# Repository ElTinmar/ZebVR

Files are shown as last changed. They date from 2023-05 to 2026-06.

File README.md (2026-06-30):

# ZebVR

Virtual reality for zebrafish.

<!---TODO
Add screenshots of the GUI
-->

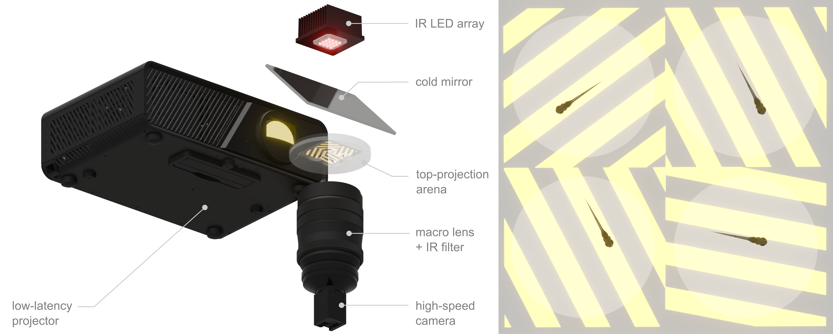
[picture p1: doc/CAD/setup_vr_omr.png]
3D render


## System requirements

This program has been tested on Ubuntu 22.04/24.04. It should run on debian-based 
distributions (apt package manager, systemd).
It should also run on Windows 10/11 but hasn't been extensively tested, and full
installation instructions on Windows are not listed here.
We recommend using a modern multicore machine with at least 32GB of RAM.
Parts of the installation process require sudo rights.
Ximea PCIe camera require Secure boot to be disabled

## Simple installation procedure on Ubuntu

```
sudo apt install git
git clone https://github.com/ElTinmar/ZebVR.git
cd ZebVR
./install.sh
```
Then reboot the computer.

Run the program with:
```
./run.sh
```

## Extra Hardware (optional)

- ViewSonic X2-4K projector
- Thorlabs PM100D
- Thorlabs CCS100
- Ximea camera 

For a full list of hardware used for the VR setup, see doc/BOM/bom.md

## Demo

This is virtual reality program and is meant to be run with a camera input.
However, for demonstration/testing purposes, the program can be run using a video file as input:

In the camera tab, select `MOVIE` in the dropdown menu, then click on `Load file`
An example movie is provided in `example/4_fish.mp4`.

## Instructions for use

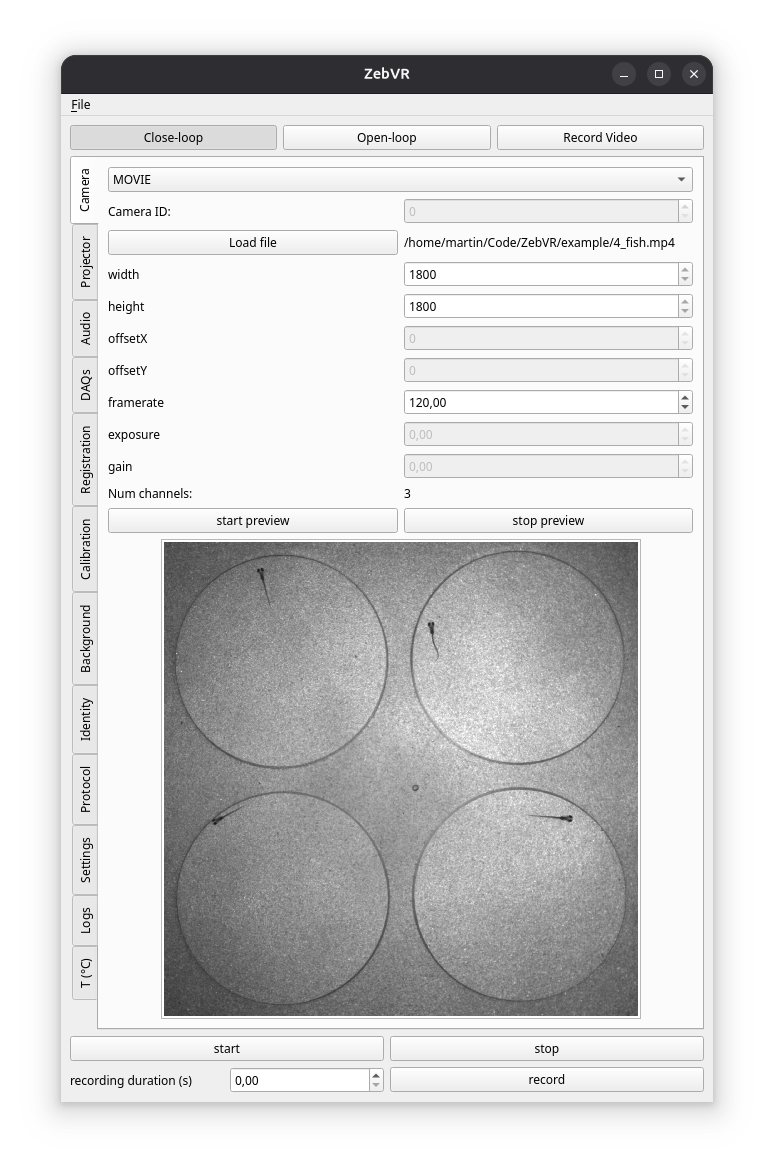
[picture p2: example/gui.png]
Screenshot of the main user interface


Select a mode:

- Close-loop: animals are tracked, the stimulus can react to fish actions in real time.
- Open-loop: no live tracking, stimulation still possible 
- Record Video: only record behavior, no stimulation

The system is configured by moving down the tabs, in order:

- Camera: Select a camera and set relevant parameters (exposure, resolution. framerate, ...). Live preview
- Projector: Select a monitor for output. Setup ViewSonic projector parameters. Run power calibration.
- Audio (optional): Select audio output and audio stream parameters.
- DAQs (optional): Select connected DAQ devices (Arduino running pyfirmata, Labjack, NI card)
- Registration: Compute transformation between camera space and screen space.
- Calibration: Calibrate camera (px/mm)
- Background: Get an image of the background, used for attributing identities, and background subtraction during live tracking
- Identity: Set a grid identify animals.
- Protocol (optional): prepare a stimulation protocol 
- Settings: enable/configure video recording. Set experiment metadata / configuration file location.
- Logs (optional): used for debugging only
- T (C) (optional): setup a temperature probe via serial port

In order to run a pre-specified protocol (setup in the Protocol tab), set a `recording duration` and hit `record`.
To specify stimulations manually on the fly, press `start` instead.
The`stop` button will stop any running experiment.

A full manual is not written yet but will be added once all features are stable. 

## Experimental features

Head-embedded VR

## Missing features

- Audio calibration
- Specify visual stimuli with irradiance units (provide a choice between floating points vs calibrated irradiance units)
- 3D environments
- better Windows installation

## Troubleshooting

### PCIe Camera No LED 

Make sure the power switch on the PCIe adapapter board is on 24V

### Ximea Error 57

if error 57 device already open, or if program is slower than usual

```bash
sudo killall python
```

### Ximea Error 56

if error 56 No Devices Found, reinstall SDK (requires sudo)

```bash
python scripts/setup_ximea.py --only-sdk
```

### libtiff.so.5: cannot open shared object file

```
sudo apt install libtiff6
cd /usr/lib/x86_64-linux-gnu/
sudo ln -s libtiff.so.6 libtiff.so.5
```

### modprobe: ERROR: could not insert 'ximea_cam_pcie': Key was rejected by service

Disable secure boot in the BIOS

### module not found

Try refreshing the environment

```
conda env update -f ZebVR.yml
```

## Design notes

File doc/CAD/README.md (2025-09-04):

# Mechanical design of the virtual reality setup

## Components

* projector: ViewSonic X2-4K
* High speed camera: Ximea MX042RG-CM-X2G2-FF 
* Infrared light
* Cold mirror
* IR filter
* Misc. Thorlabs parts

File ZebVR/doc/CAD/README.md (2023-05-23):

# Mechanical design of the virtual reality setup

## Components

* projector: Texas Instrument DLP Lightcrafter 4500
* High speed camera: Ximea MX042RG-CM-X2G2-FF 
* Infrared light
* Cold mirror
* IR filter
* Misc. Thorlabs parts

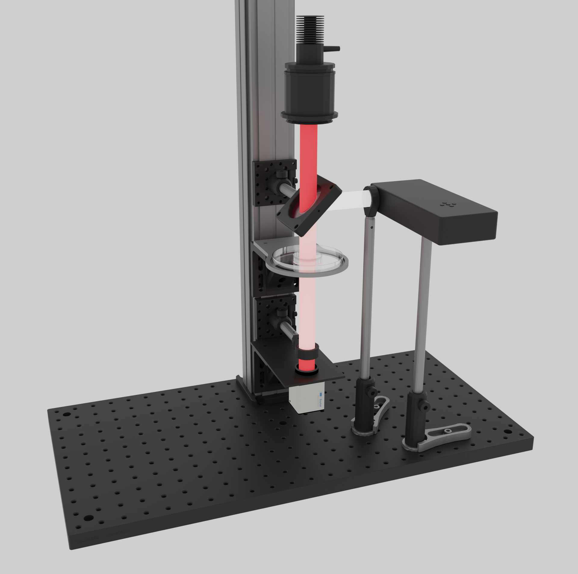
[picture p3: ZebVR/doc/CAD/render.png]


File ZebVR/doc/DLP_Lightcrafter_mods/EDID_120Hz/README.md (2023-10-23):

# Setting up the lightcrafter to display at 120 Hz

The EDID is programmed at the factory with resolutions of 1280 x 800 and 912 x 1140 at 60 Hz.
To make the display available at 120 Hz, it is recommended to update the EDID on the device.

## 1. Set the J8 jumper to enable writing to EDID EEPROM

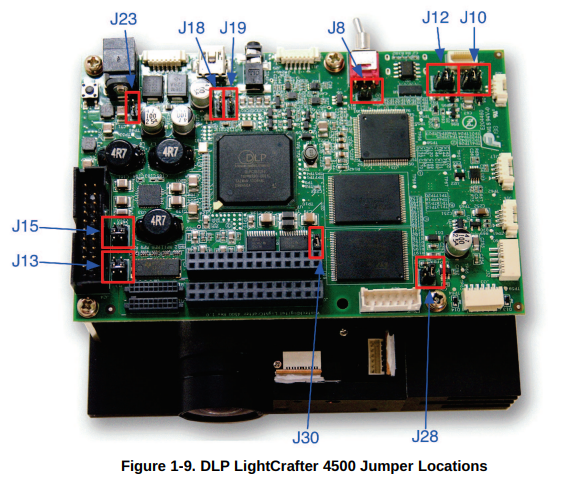
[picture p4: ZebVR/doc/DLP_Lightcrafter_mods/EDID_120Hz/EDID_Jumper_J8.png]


Source: https://www.ti.com/lit/ug/dlpu011f/dlpu011f.pdf

## 2. Install programms to read and write the EEPROM via I2C through the HDMI cable

```
sudo apt install ghex
sudo apt install read-edid
sudo apt install i2c-tools
```

## 3. Make a backup of the original EDID

Plug the HDMI cable in the Lightcrafter and your machine. The EEPROM can be accessed 
even if the Lightcrafter is turned off.

### 3.1 Identify on which I2C bus the Lightcrafter is

List all the I2C buses:

```
i2cdetect -l
```

If necessary try to access EDID for each detected device using 

```
sudo get-edid -b X | parse-edid 
```

replace X by the bus number identified earlier, in my case it was

```
sudo get-edid -b 2 | parse-edid 
```

### 3.1 Dump EDID to a file

Once you have found the right bus, save the EDID to a file

```
sudo get-edid -b 2 > original.bin 
``` 

You can check and modify the content of the file using an hexadecimal editor such as ghex.

## 4. Modify the EDID to advertize 912 x 1140 at 120 Hz

The VESA EDID 1.3 specification can be downloaded from here https://vesa.org/vesa-standards/ 
and details the organization of the 256 bytes. This is a useful resource should you 
wish to implement other resolutions (especially the "Detailed Timing Descriptor" section).

## 4.1 Required timings

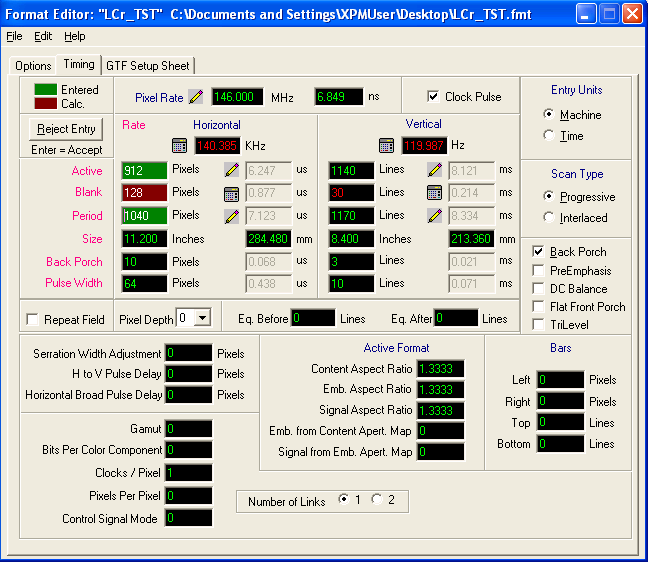
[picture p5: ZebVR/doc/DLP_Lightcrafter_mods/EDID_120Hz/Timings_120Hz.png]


Source: https://e2e.ti.com/support/dlp-products-group/dlp/f/dlp-products-forum/699749/dlplcr4500evm-120hz-output-in-video-mode-is-choppy

## 4.2 Flashing the EEPROM

Be EXTREMELY careful when you flash the device, if you select the wrong I2C bus you
could permanently damage your computer. Do at your own risk. You have been warned.
I mean seriously.

```
sudo i2cset 2 0x50 0x5A 0x08 b # Pixel Clock first 8 bits | 146MHz -> 14600 -> 0x39 0x08
sudo i2cset 2 0x50 0x5B 0x39 b # Pixel Clock last 8 bits
sudo i2cset 2 0x50 0x5C 0x90 b # Horizontal active lower 8 bits | 912
sudo i2cset 2 0x50 0x5D 0x80 b # Horizontal blanking lower 8 bits | 128
sudo i2cset 2 0x50 0x5E 0x30 b # Horizontal active upper 4 bits, Horizontal blanking upper 4 bits
sudo i2cset 2 0x50 0x5F 0x74 b # Vertical active lower 8 bits | 1140
sudo i2cset 2 0x50 0x60 0x1E b # Vertical blanking lower 8 bits | 30
sudo i2cset 2 0x50 0x61 0x40 b # Vertical active upper 4 bits, Vertical blanking upper 4 bits
sudo i2cset 2 0x50 0x62 0x0A b # Horizontal Sync Offset (Back porch), lower 8 bits | 10
sudo i2cset 2 0x50 0x63 0x40 b # Horizontal Sync pulse width, lower 8 bits | 64
sudo i2cset 2 0x50 0x64 0x3A b # Vertical Sync Offset (Back porch) lower 4 bits, Vertical Sync pulse width lower 4 bits | 3, 10
sudo i2cset 2 0x50 0x65 0x00 b # bit 7,6: Horizontal Sync Offset upper 2 bits, bit 5,4: Horizontal Sync pulse width upper 2 bits, bits 3,2: Vertical Sync Offset upper 2 bits, bits 1,0: Vertical Sync pulse width upper 2 bits
sudo i2cset 2 0x50 0x66 0x1C b # Horizontal Image Size (mm), lower 8 bits | 284
sudo i2cset 2 0x50 0x67 0xD5 b # Vertical Image Size (mm), lower 8 bits | 213
sudo i2cset 2 0x50 0x68 0x10 b # Horizontal Image Size upper 4 bits, Vertical Image Size upper 4 bits
sudo i2cset 2 0x50 0x69 0x00 b # Horizontal border | 0
sudo i2cset 2 0x50 0x6A 0x00 b # Vertical border | 0
sudo i2cset 2 0x50 0x6B 0x1E b # Flags
sudo i2cset 2 0x50 0x7F 0x55 b # Checksum
```

Check that the flash was successful:

```
sudo get-edid -b 2 | parse-edid 
```

You should now be able to see the line:

```
Modeline     "Mode 2" 146.00 912 922 986 1040 1140 1143 1153 1170 +hsync +vsync
```

This procedure can be adapted to add other resolutions, a good understanding 
of the EDID specification will be necessary.

You should now be able to select 912 x 1140 at 120 Hz in the display 
settings when you plug in the Lightcrafter to a (relatively recent) computer.

# 5. Use the DLP Lightcrafter Pattern mode for 120 Hz display

Only 8-bit grayscale is possible in Pattern mode @120Hz

For some reason, the 120 Hz display rate doesn't seem to work in video mode 
(the Lightcrafter reports a buffer freeze and the image is very choppy), contrary
to what is advertised in the documentation.
It does work in 8-bit pattern mode with input from the HDMI and triggers on VSYNC
however, so be sure to select that mode, and dial in an exposure of 8333 or less
(maximum duration of a frame at 120 Hz).

# 6. Aspect ratio

The DMD array is diagonal and not orthogonal. This messes up the aspect ratio in native
resolution, and must be accounted for by scaling the patterns

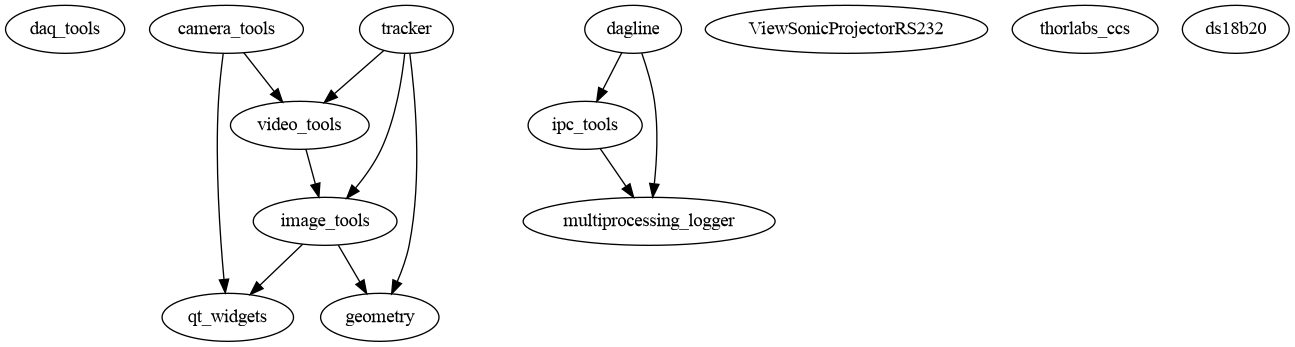
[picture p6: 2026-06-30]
doc/custom_dependencies.png

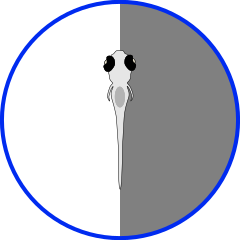
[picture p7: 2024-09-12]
ZebVR/analysis/phototaxis_darkright.png

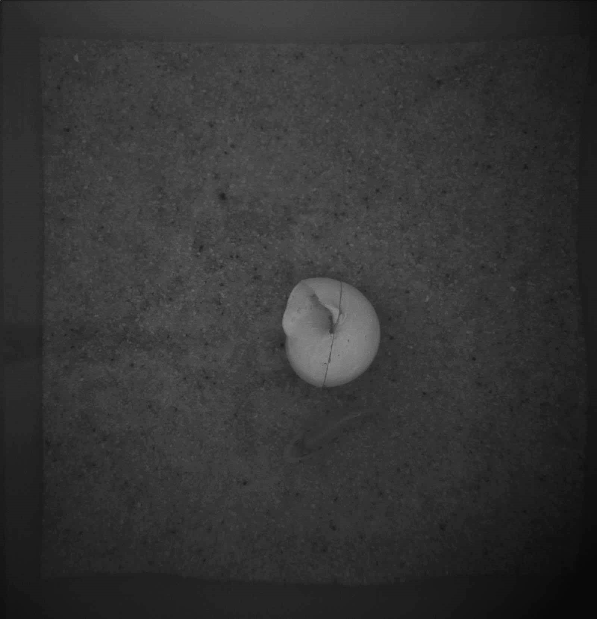
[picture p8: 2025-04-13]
ZebVR/textures/shell_phase_2_vertical.jpg

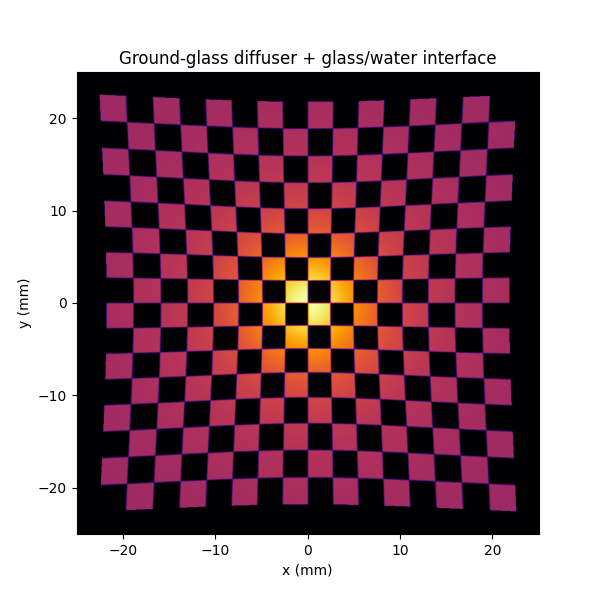
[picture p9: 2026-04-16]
ZebVR/simulations/glass_water_image.png

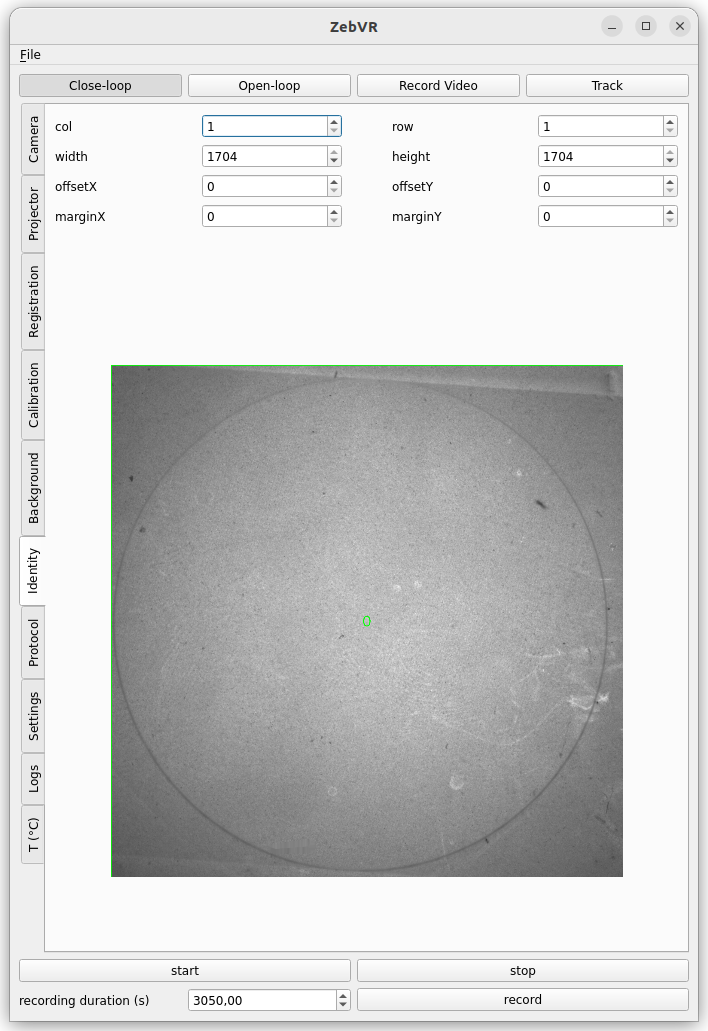
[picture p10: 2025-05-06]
ZebVR/resources/identity_tab_closedloop_1fish.png

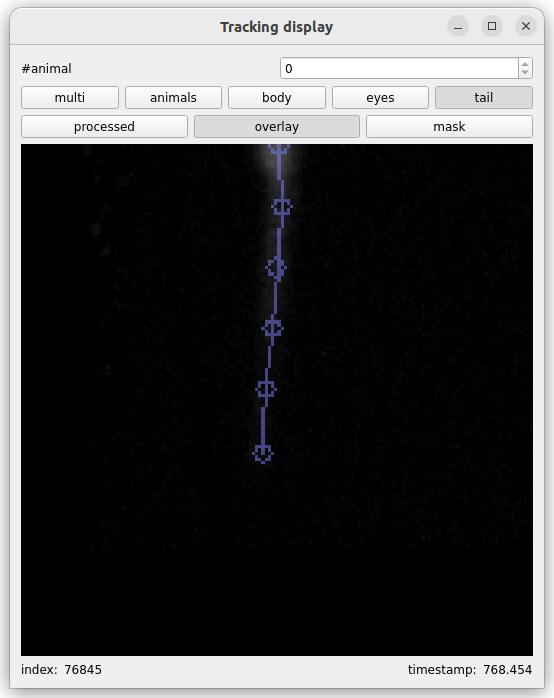
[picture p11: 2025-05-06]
ZebVR/resources/tracking_tail_overlay.png

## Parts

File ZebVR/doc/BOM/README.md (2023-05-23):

# Bill of Materials

Contains the list of hardware that was used to create the virtual reality setup

TODO: markdown table with links to parts

| Part name     | Link          | Approx price | 
| ------------- | ------------- |--------------|
| Content Cell  | Content Cell  |              |
| Content Cell  | Content Cell  |              |

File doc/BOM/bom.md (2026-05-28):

| system | subsystem | manufacturer / seller | description | parts name / ref | num parts | link | estimated price per part | total price |
| --- | --- | --- | --- | --- | --- | --- | --- | --- |
| mechanical | breadboard | Thorlabs | main breadboard | MB4545/M | 1 | https://www.thorlabs.com/item/MB4545_M | 303.58 | 303.58 |
| mechanical | main column | Thorlabs | 34mm column | XT34-1000 | 1 | https://www.thorlabs.com/item/XT34-1000 | 106.87 | 106.87 |
| mechanical | main column | Thorlabs | dovetail plates | XT34HP/M | 7 | https://www.thorlabs.com/item/XT34HP_M | 60.96 | 426.72 |
| mechanical | main column | Thorlabs | post holder 75mm | PH75/M | 3 | https://www.thorlabs.com/item/PH75_M | 9.35 | 28.05 |
| mechanical | main column | Thorlabs | post 75mm | TR75/M | 3 | https://www.thorlabs.com/item/TR75_M | 5.98 | 17.94 |
| mechanical | main column | Thorlabs | post holder 50mm | PH50/M | 3 | https://www.thorlabs.com/item/PH50_M | 8.71 | 26.13 |
| mechanical | main column | Thorlabs | post 50mm | TR50/M | 3 | https://www.thorlabs.com/item/TR50_M | 5.74 | 17.22 |
| mechanical | main column/projector column | Thorlabs | vertical mounting plate | XT66P1 | 2 | https://www.thorlabs.com/item/XT66P1 | 41.02 | 82.04 |
| mechanical | projector column | Thorlabs | 66mm column | XT66-750 | 1 | https://www.thorlabs.com/item/XT66-750 | 116.92 | 116.92 |
| mechanical | projector column | Thorlabs | 66mm column | XT66-200 | 1 | https://www.thorlabs.com/item/XT66-200 | 59.8 | 59.8 |
| mechanical | projector column | Thorlabs | right angle bracket | XT66RA2 | 1 | https://www.thorlabs.com/item/XT66RA2 | 47.09 | 47.09 |
| mechanical | projector column | Thorlabs | double dovetail clamp | XT66C2 | 2 | https://www.thorlabs.com/item/XT66C2 | 24.91 | 49.82 |
| mechanical | projector column | Thorlabs | dovetail plate | XT66P2/M | 1 | https://www.thorlabs.com/item/XT66P2_M | 79.16 | 79.16 |
| mechanical | projector column | Thorlabs | horizontal mounting plate | XT66P3 | 1 | https://www.thorlabs.com/item/XT66P3 | 62.68 | 62.68 |
| mechanical | projector column | Thorlabs | projector breadboard | MB3045/M | 1 | https://www.thorlabs.com/item/MB3045_M | 209.79 | 209.79 |
| illumination | LED | Intelligent LED Solutions | high power IR LED array | ILR-IO16-85NL-SC201-WIR200 | 1 | https://de.rs-online.com/web/p/ir-leds/7732912 | 106.21 | 106.21 |
| illumination | power supply | Mean Well | LED driver / power supply | LPF-25D-24 | 1 | https://de.rs-online.com/web/p/led-treiber/7647271 | 41.48 | 41.48 |
| illumination | cold mirror | Edmund Optics | cold mirror | #64-452  | 1 | https://www.edmundoptics.de/p/45deg-aoi-101-x-127mm-cold-mirror/19164/ | 238 | 238 |
| projector | screen | EdmundOptics | ground glass diffuser | #49-159 | 2 | https://www.edmundoptics.de/p/50-x-50mm-uv-fused-silica-ground-glass-optical-diffuser/9502/ | 115 | 230 |
| projector | projector | ViewSonic | 240Hz projector | X2-4KE Pro | 1 | https://www.visunext.de/p/viewsonic-x2-4ke-pro-beamer-1000033494/ | 1678.99 | 1678.99 |
| projector | UV mod | Luminus Devices | UV LED | CBM-50X-UV-Y31-FA380-22 | 1 | https://www.mouser.de/ProductDetail/Luminus-Devices/CBM-50X-UV-Y31-FA380-22?qs=tlsG%2FOw5FFgEjhF0xGTq5w%3D%3D | 237.11 | 237.11 |
| projector | UV mod | Molex | power cable | 218396-1080 | 1 | https://www.mouser.de/ProductDetail/Molex/218396-1080?qs=XAiT9M5g4x96QOBtZ0G04Q%3D%3D | 2.77 | 2.77 |
| projector | UV mod | JLCPCB | power adapter board | PicoSpoxAdapter_v2 | 1 | https://github.com/ElTinmar/ZebVR/tree/dev/PCB_X2-4K_UV_mod | 40 | 40 |
| projector | UV mod | Molex | connector 10pin | 87438-1043 | 10 | https://www.mouser.de/ProductDetail/Molex/87438-1043?qs=yoOJgkCG%2FJuVV3eNIak6LQ%3D%3D | 0.851 | 8.51 |
| projector | UV mod | Molex | connector 8pin | 87438-0843 | 10 | https://www.mouser.de/ProductDetail/Molex/87438-0843?qs=JAINH4q0Y0FNXejwT7VIEw%3D%3D | 0.765 | 7.65 |
| projector | cable | StarTech | HDMI 2.0 | HDMI2-CABLE-4K60-2M | 1 | https://de.rs-online.com/web/p/hdmi-kabel/0473429 | 14.27 | 14.27 |
| projector | cable | StarTech | RS-232 female to USB male (crossover / null-modem) | ICUSB232FTN | 1 | https://www.startech.com/de-de/karten-adapter/icusb232ftn | 47.55 | 47.55 |
| camera | lens | EdmundOptics | C-mount adapter | #54-341 | 1 | https://www.edmundoptics.com/p/c-mount-nikon-f-mount-camera-lens-adapter/11135/ | 85 | 85 |
| camera | lens | Venus | 60mm macro lens | Laowa 60mm f/2.8 2X Ultra-Macro (Nikon F-mount version) | 1 | https://www.venuslens.net/product/laowa-60mm-f2/ | 400 | 400 |
| camera | lens | Hoya | IR filter | HOYA INFRARED R72 (62mm) | 1 | https://hoya-filter.eu/de/effektfilter/577-hoya-infrared-r72-infrarotfilter-62mm-0024066015464.html | 50.99 | 50.99 |
| camera | camera | Ximea | high speed IR camera | MX042RG-CM-X2G2 | 1 | https://www.ximea.com/products/embedded-system/xix-embedded-vision-multiple-cameras/cmosis-cmv4000-pcie-b-w-nir-embedded-camera | 1750 | 1750 |
| camera | interface | Ximea | PCIe firefly board | HA-2P-X4G3-FF-X8G3 | 1 | https://www.ximea.com/accessories/hostadapters/host-adapter-with-2-ports-for-pcie-gen-3-x4-firefly-cables | 500 | 500 |
| camera | cable | Ximea | firefly cable | CBL-ECUE-X4G3-2M0 | 1 | https://www.ximea.com/accessories/cables/2-0m-firefly-cable-for-xix-cameras-pcie-gen-3-x4 | 20 | 20 |
| computer | computer | Corsair | case | Corsair Frame 4000D | 1 | https://www.mindfactory.de/product_info.php/Corsair-Frame-4000D-Midi-Tower-ohne-Netzteil-schwarz_1612286.html | 84.66 | 84.66 |
| computer | computer | MSI | motherboard | MSI X870E Gaming Plus WIFI AMD X870E | 1 | https://www.mindfactory.de/product_info.php/MSI-X870E-Gaming-Plus-WIFI-AMD-X870E-So-AM5-DDR5-ATX-Retail_1617259.html | 249.87 | 249.87 |
| computer | computer | AMD | CPU | AMD Ryzen 9 9950X | 1 | https://www.mindfactory.de/product_info.php/AMD-Ryzen-9-9950X-16x-4-30GHz-So-AM5-WOF_1538191.html | 512.82 | 512.82 |
| computer | computer | Noctua | CPU Cooler | Noctua NH-D15 | 1 | https://www.mindfactory.de/product_info.php/Noctua-NH-D15-Tower-Kuehler_958701.html | 108.69 | 108.69 |
| computer | computer | NVIDIA | GPU | GeForce RTX 5070Ti | 1 | https://www.mindfactory.de/product_info.php/16GB-INNO3D-GeForce-RTX-5070-Ti-X3-Aktiv-PCIe-5-0-x16--Retail-_1615596.html | 949 | 949 |
| computer | computer | G. Skill | RAM | 64GB G.Skill F5-6000J3040G32GX2-RS5W | 1 | https://www.mindfactory.de/product_info.php/64GB-G-Skill-Ripjaws-S5-weiss-DDR5-6000-DIMM-CL30-Dual-Kit_1474164.html | 1076.97 | 1076.97 |
| computer | computer | Samsung | nvme storage | Samsung 990 PRO 1 TB | 1 | https://www.mindfactory.de/product_info.php/1TB-Samsung-990-PRO-M-2-PCIe-4--3D-NAND-TLC--MZ-V9P1T0BW-_1471173.html | 189 | 189 |
| computer | computer | Seagate | HDD | 6TB Seagate IronWolf | 1 | https://www.mindfactory.de/product_info.php/6TB-Seagate-IronWolf-ST6000VN006-256MB-3-5Zoll--8-9cm--SATA-6Gb-s_1478263.html | 203.86 | 203.86 |
| computer | computer | Seasonic | power supply | Seasonic Vertex PX-850 | 1 | https://www.mindfactory.de/product_info.php/850-Watt-Seasonic-Vertex-PX-850-Modular-80--Platinum_1511793.html | 207.81 | 207.81 |
| computer | computer | Noctua | fans | Noctua NF-A14 PWM | 4 | https://www.mindfactory.de/product_info.php/Noctua-NF-A14-PWM-chromax-black-swap-140x140x25mm-300-1500-U-min-24-6-d_1203222.html | 28.85 | 115.4 |
| measurement | powermeter console | Thorlabs | powermeter console | PM100D (discontinued) / PM100D2 | 1 | https://www.thorlabs.com/item/pm100d | 1200 | 1200 |
| measurement | photodiode sensor | Thorlabs | photodiode sensor | S120VC | 1 | https://www.thorlabs.com/item/S120VC | 480.64 | 346.64 |
| measurement | spectrophotometer | Thorlabs | spectrophotometer | CCS100 (discontinued) / CCT11 | 1 | https://www.thorlabs.com/item/ccs100 | 3000 | 3000 |
|  |  |  |  |  |  |  |  |  |
|  | SYSTEM TOTAL | CUMULATIVE TOTAL |  |  |  |  |  |  |
| mechanical | 1633.81 | 1633.81 |  |  |  |  |  |  |
| illumination | 385.69 | 2019.5 |  |  |  |  |  |  |
| projector | 2245.29 | 4264.79 |  |  |  |  |  |  |
| camera | 2805.99 | 7070.78 |  |  |  |  |  |  |
| computer | 3698.08 | 10768.86 |  |  |  |  |  |  |
| measurement | 4680.64 | 15449.5 |  |  |  |  |  |  |

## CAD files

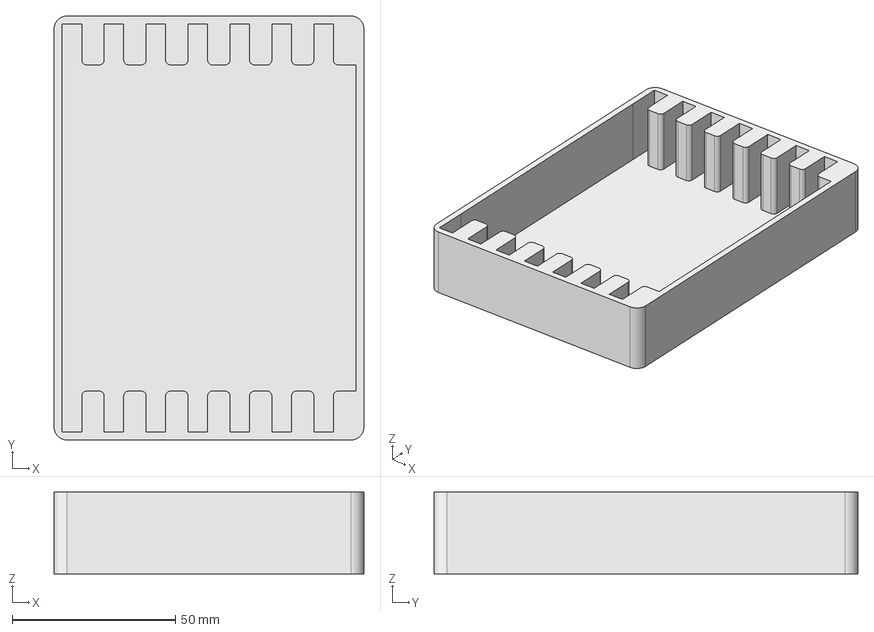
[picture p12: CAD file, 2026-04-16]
doc/CAD/agarose_stamps/mold_organizer.FCStd
95.0 x 130.0 x 25.0 mm

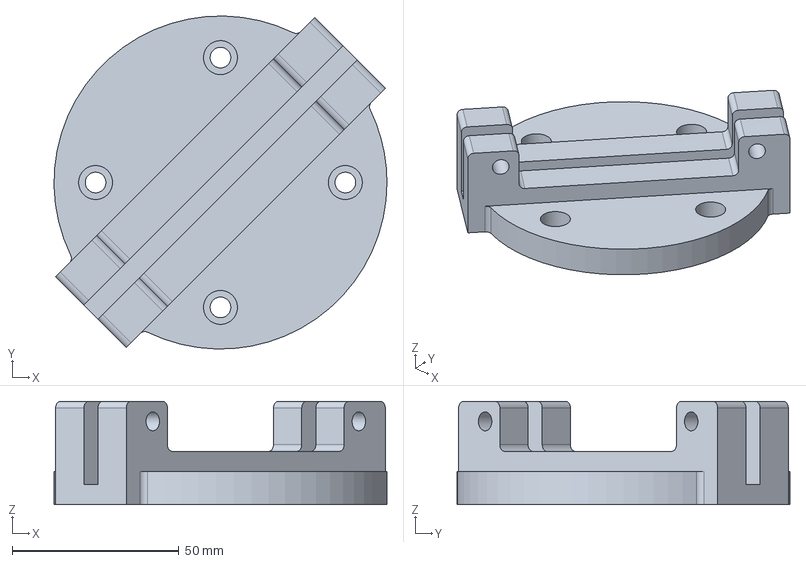
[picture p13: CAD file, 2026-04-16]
doc/CAD/cold_mirror_holder/mirror_holder_v2.FCStd
100.0 x 100.0 x 31.0 mm

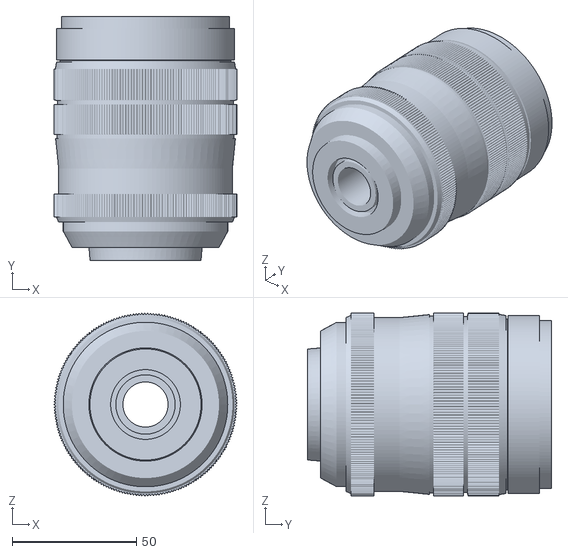
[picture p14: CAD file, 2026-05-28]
doc/CAD/laowa_venus_60mm_f2-8_macro.stl
73.5 x 98.1 x 73.5

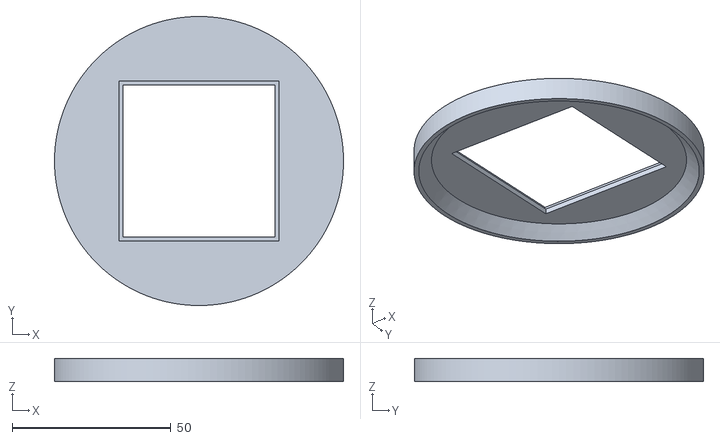
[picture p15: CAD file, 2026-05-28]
doc/CAD/sample_platform/calibration_jig_91mm-BodyChamfer.stl
91.0 x 91.0 x 7.35

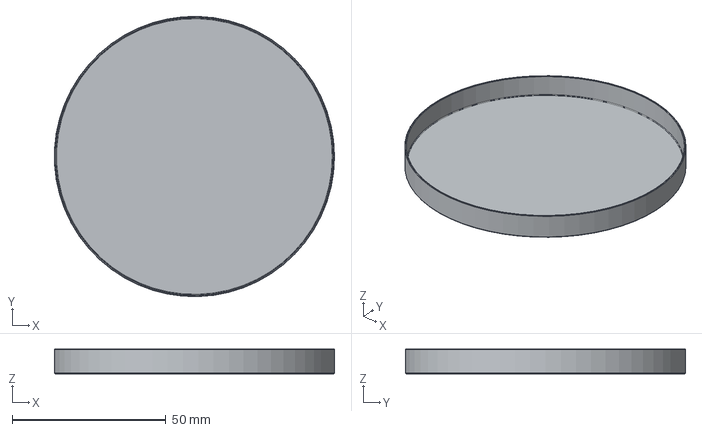
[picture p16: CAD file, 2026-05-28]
doc/CAD/setup/PetridishLid.stp
90.9 x 91.0 x 8.00 mm

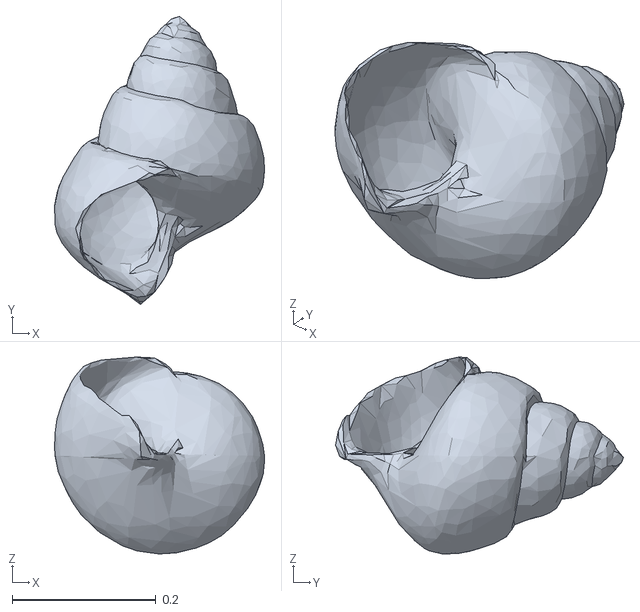
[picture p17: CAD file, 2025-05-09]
ZebVR/resources/shell_simplified.obj
0.292 x 0.4 x 0.274

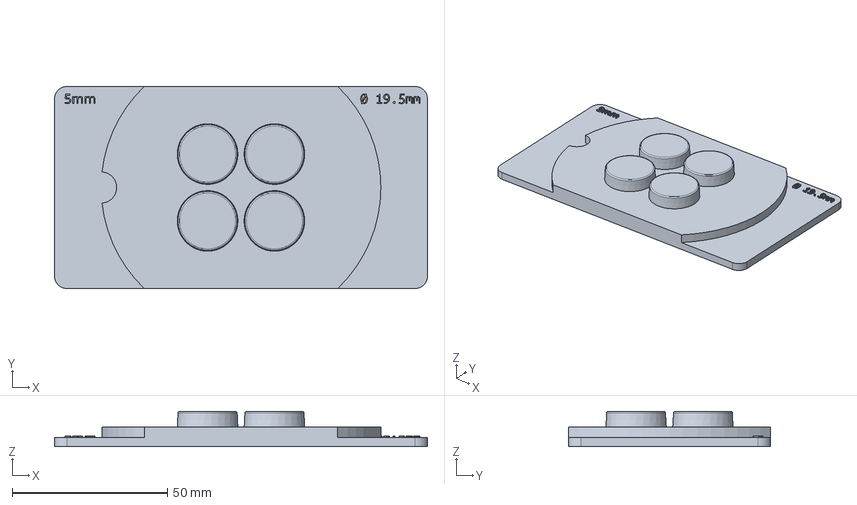
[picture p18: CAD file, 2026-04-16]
doc/CAD/agarose_stamps/agarose_mold_single_circle_2x2_45mm_depth_5mm.FCStd
120.0 x 65.0 x 11.4 mm

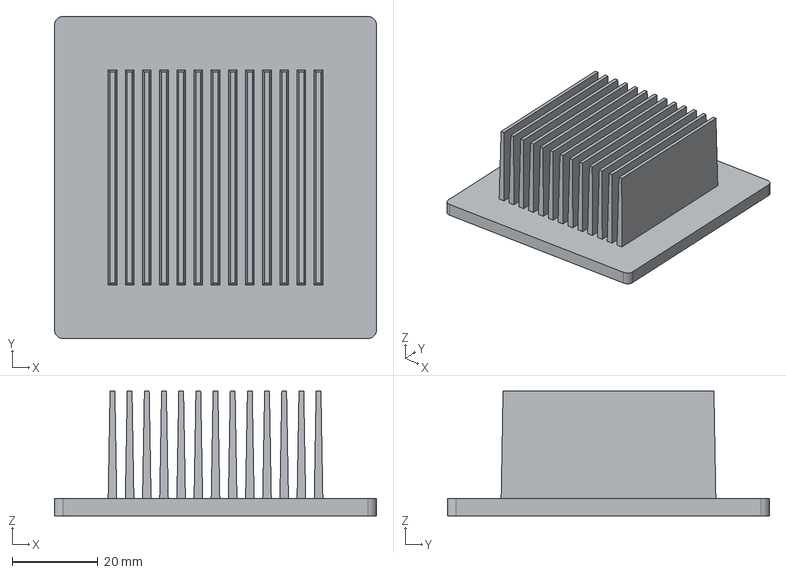
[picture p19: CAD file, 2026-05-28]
doc/CAD/setup/HeatSink.stp
75.0 x 75.0 x 29.0 mm

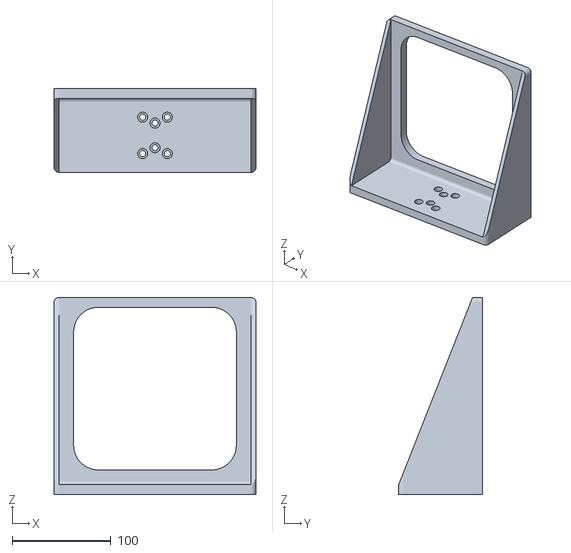
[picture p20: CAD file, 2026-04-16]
doc/CAD/sample_platform/slim_3d_print-Platform_large.stl
205.0 x 85.0 x 200.0

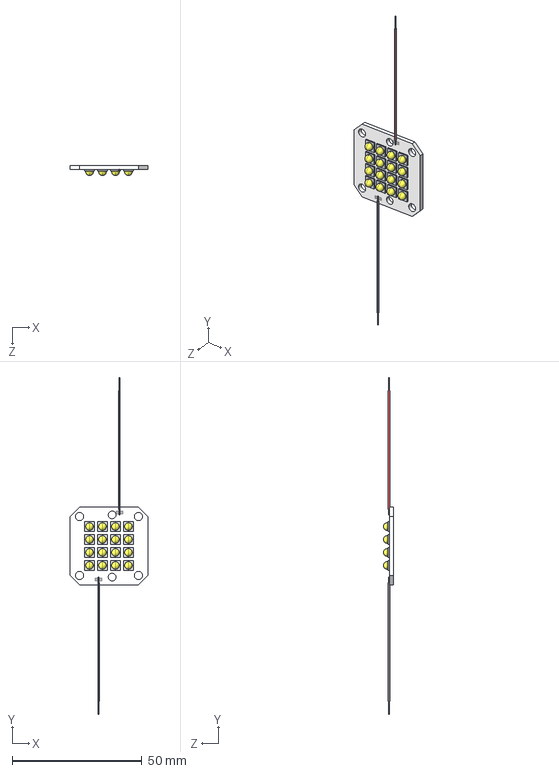
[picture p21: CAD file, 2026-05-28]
doc/CAD/setup/ILR-ON16-SC211-WIR200.stp
30.0 x 130.0 x 3.95 mm

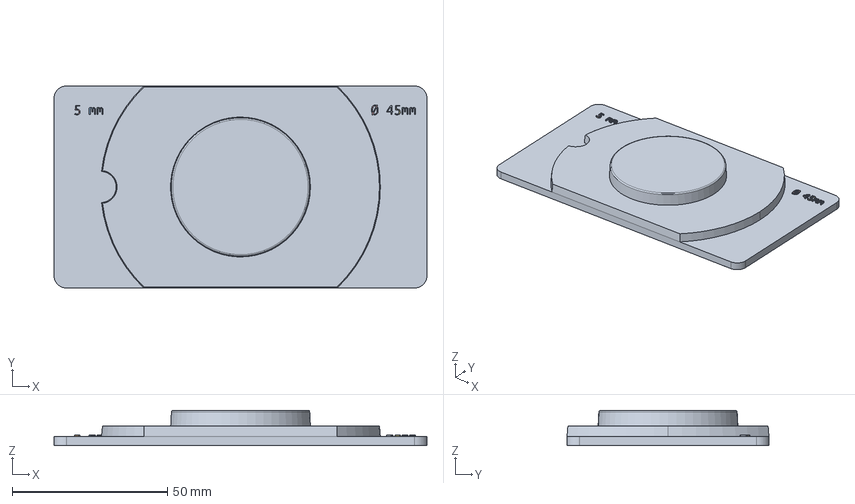
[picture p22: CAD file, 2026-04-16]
doc/CAD/agarose_stamps/agarose_mold_single_circle_45mm_depth_5mm.FCStd
120.0 x 65.0 x 11.4 mm

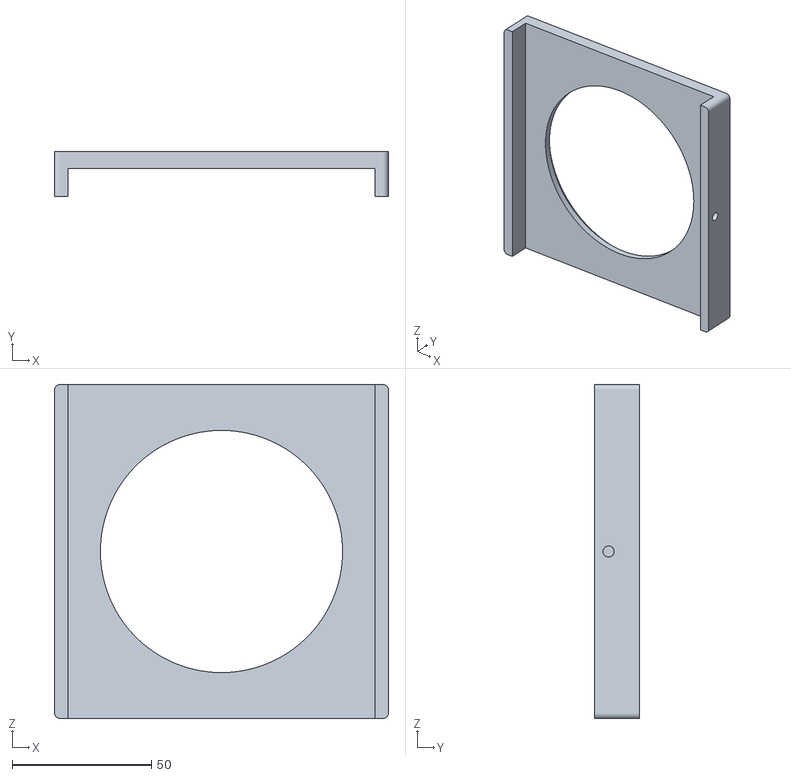
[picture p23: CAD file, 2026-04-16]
doc/CAD/sample_platform/slim_3d_print_tray.stl
120.0 x 16.0 x 120.0

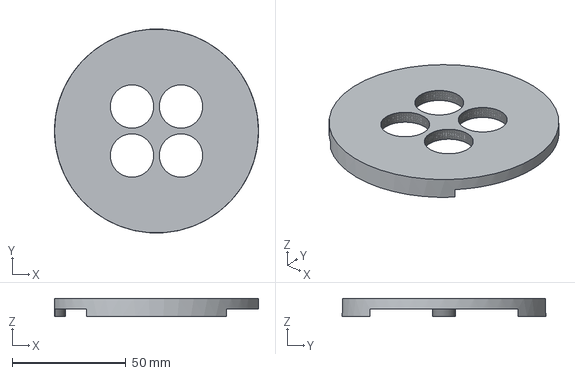
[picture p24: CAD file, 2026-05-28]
doc/CAD/setup/GelArena4Wells.stp
89.5 x 89.3 x 8.00 mm

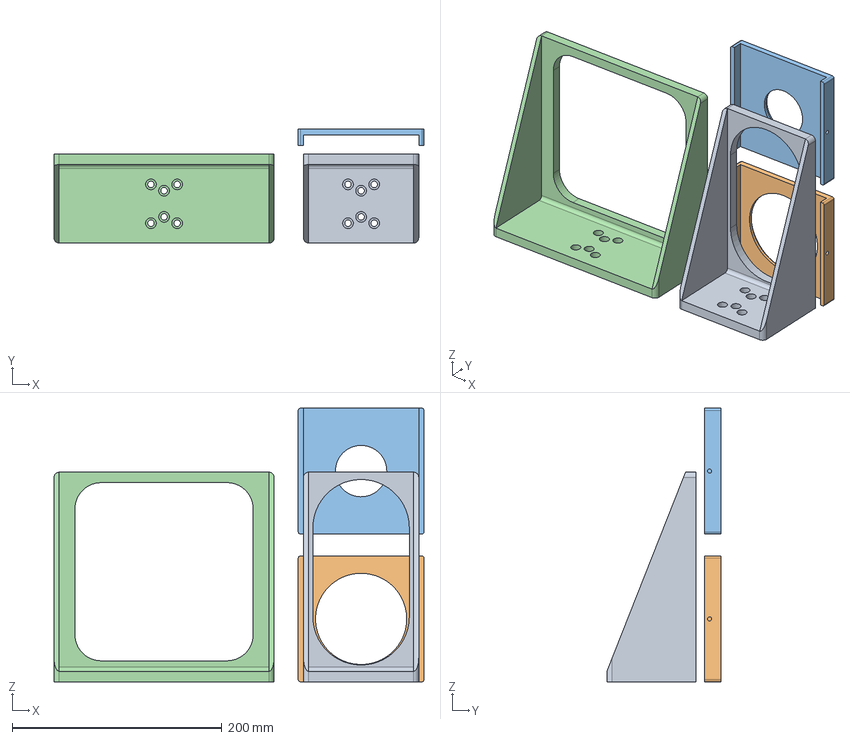
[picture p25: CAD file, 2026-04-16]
doc/CAD/sample_platform/slim_3d_print.FCStd
353.0 x 109.0 x 261.0 mm
Platform_small
Lid_Petri
Lid_2in
Platform_large

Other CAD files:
doc/CAD/cold_mirror_holder/mirror_holder_v2-BodyFillet.stl
doc/CAD/sample_platform/calibration_jig_91mm.FCStd
doc/CAD/agarose_stamps/mold_organizer-BodyFillet001.stl
doc/CAD/setup/step_64452_cold_mirror.step
doc/CAD/agarose_stamps/agarose_mold_single_circle_2x2_45mm_depth_5mm.stl
doc/CAD/agarose_stamps/agarose_mold_single_circle_45mm_depth_5mm.stl
doc/CAD/sample_platform/slim_3d_print-Lid_2in.stl
doc/CAD/sample_platform/slim_3d_print-Platform_small.stl
doc/CAD/setup/AP25E6M-Step.step
doc/CAD/setup/MB3045_M-Step.step
doc/CAD/setup/PH50_M-Step.step
doc/CAD/setup/PH75_M-Step.step
doc/CAD/setup/XT34-1000-Step.step
doc/CAD/setup/XT34HP_M-Step.step
doc/CAD/setup/XT66-200-Step.step
doc/CAD/setup/XT66-750-Step.step
doc/CAD/setup/XT66C2-Step.step
doc/CAD/setup/XT66P1-Step.step
doc/CAD/setup/XT66P2_M-Step.step
doc/CAD/setup/XT66P3-Step.step
doc/CAD/setup/XT66RA2-Step.step
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

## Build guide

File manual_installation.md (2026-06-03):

## Software dependencies

### deb packages on Ubuntu

```bash
sudo apt-get install libportaudio2 build-essential libusb-1.0-0-dev git
```

### Labjack exodriver

On Ubuntu:
```bash
git clone https://github.com/labjack/exodriver.git
cd exodriver/
sudo ./install.sh
cd .. 
rm -rf exodriver
```

Windows: https://files.labjack.com/installers/LJM/Windows/x86_64/release/LabJack_2024-05-16.exe

## Installation instructions

Solving the environment might take a few minutes.

```bash
git clone https://github.com/ElTinmar/ZebVR.git
cd ZebVR
conda env create -f ZebVR.yml
conda activate ZebVR
```

A full list of dependencies with version number can be found in requirements.txt

### Install camera SDK and python bindings into environment

#### XIMEA

The SDK and python binding URLs are hardcoded in the script and will break
if the camera manufacturers decide to change their website layout. The SDK 
can be manually downloaded from the manufacturer website, and the python module placed
in the conda environment site-packages folder (e.g. /home/user/miniconda3/envs/ZebVR/lib/python3.13/site-packages/ximea)

```bash
conda activate ZebVR
python scripts/setup_ximea.py
python scripts/setup_spinnaker.py
```

You can also install the SDK (requires sudo) or python bindings separately:

```bash
python scripts/setup_ximea.py --only-sdk
python scripts/setup_spinnaker.py --only-sdk
```

```bash
conda activate ZebVR
python scripts/setup_ximea.py --only-python
python scripts/setup_spinnaker.py --only-python
```

Please note that every time a new kernel is installed during a system update,
the SDK needs to be reinstalled.

##### Automated XIMEA Driver Maintenance

After the drivers have been installed once (see steps above), to prevent the XIMEA camera driver from breaking during Ubuntu kernel updates, 
install the automated maintenance service:

```bash
sudo chmod +x install_ximea_systemd_service.sh
sudo ./install_ximea_systemd_service.sh
```

Secure boot might need to be disabled.

#### Aravis

```bash
conda activate ZebVR
git clone https://github.com/AravisProject/aravis.git
cd aravis 
meson setup build --prefix=$CONDA_PREFIX -Dintrospection=enabled -Dviewer=disabled -Dtests=true --libdir=lib
ninja -C build install
cd ..
rm -rf aravis
```

### Thorlabs hardware 

This is needed to communicate with Thorlabs spectrophotometer and power measurement unit 
for automated power measurements.

```bash
sudo apt install innoextract
python -m thorlabs_ccs.get_firmware
```

set udev rule for all Thorlabs devices:

```bash
sudo tee /etc/udev/rules.d/99-thorlabs.rules > /dev/null << 'EOF'
SUBSYSTEMS=="usb", ATTRS{idVendor}=="1313", GROUP="plugdev", MODE="0666"
EOF
```

Reload udev rules:

```bash
sudo udevadm control --reload-rules
sudo udevadm trigger
```

### Permissions to access hardware

```bash
sudo usermod -a -G plugdev,dialout "$USER"
```

## Running the software 

```bash
conda activate ZebVR
python -m ZebVR
```

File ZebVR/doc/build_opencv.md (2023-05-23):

# Why would you want to compile opencv yourself ?

opencv-python in PyPI doesn't ship with a lot of codec because of licensing issues.

# Go to conda environment

This is important, everything has to be done in the proper conda environment 

```
conda activate VirtualReality
```

# Install dependencies

```
sudo apt install build-essential cmake pkg-config unzip yasm git checkinstall \
libjpeg-dev libpng-dev libtiff-dev \
libgstreamer1.0-dev libgstreamer-plugins-base1.0-dev \
libxvidcore-dev x264 libx264-dev libfaac-dev libmp3lame-dev libtheora-dev \
libfaac-dev libmp3lame-dev libvorbis-dev \
libgtk-3-dev libtbb-dev libatlas-base-dev gfortran \
libavcodec-dev libavformat-dev libavutil-dev libswscale-dev
```

# Download sources

Adapt to the version of opencv you want to install

```
wget -O opencv.zip https://github.com/opencv/opencv/archive/refs/tags/4.7.0.zip
wget -O opencv_contrib.zip  https://github.com/opencv/opencv_contrib/archive/refs/tags/4.7.0.zip
unzip opencv.zip
unzip opencv_contrib.zip
cd opencv-4.7.0
mkdir build
cd build
```

# Configure 

Modify OPENCV_EXTRA_MODULES_PATH accordingly

```
cmake -D WITH_CUDA=OFF \
-D BUILD_TIFF=ON \
-D BUILD_opencv_java=OFF \
-D WITH_OPENGL=ON \
-D WITH_OPENCL=ON \
-D WITH_IPP=ON \
-D WITH_TBB=ON \
-D WITH_EIGEN=ON \
-D WITH_V4L=ON \
-D WITH_VTK=OFF \
-D BUILD_TESTS=OFF \
-D BUILD_PERF_TESTS=OFF \
-D CMAKE_BUILD_TYPE=RELEASE \
-D BUILD_opencv_python2=OFF \
-D CMAKE_INSTALL_PREFIX=/usr/local \
-D PYTHON3_INCLUDE_DIR=$(python3 -c "from distutils.sysconfig import get_python_inc; print(get_python_inc())") \
-D PYTHON3_PACKAGES_PATH=$(python3 -c "from distutils.sysconfig import get_python_lib; print(get_python_lib())") \
-D INSTALL_C_EXAMPLES=ON \
-D INSTALL_PYTHON_EXAMPLES=ON \
-D OPENCV_ENABLE_NONFREE=ON \
-D OPENCV_GENERATE_PKGCONFIG=ON \
-D PYTHON3_EXECUTABLE=$(which python3) \
-D PYTHON_DEFAULT_EXECUTABLE=$(which python3) \
-D OPENCV_EXTRA_MODULES_PATH=/home/martin/Downloads/opencv_contrib-4.7.0/modules \
-D BUILD_EXAMPLES=ON ..
```

# Make sure configuration is correct

Look for the Python section in the output, it should look something like this

```
-- Python 3:
--  Interpreter:  /home/martin/miniconda3/envs/VirtualReality/bin/python3 (ver 3.8.16)
--  Libraries:    /home/martin/miniconda3/envs/VirtualReality/lib/libpython3.8.so (ver 3.8.16)
--  numpy:        /home/martin/miniconda3/envs/VirtualReality/lib/python3.8/site-packages/numpy/core/include (ver 1.24.2)
--  install path: /home/martin/miniconda3/envs/VirtualReality/lib/python3.8/site-packages/cv2/python-3.8
```

# Compile and install

```
make -j10
sudo make install
sudo ldconfig
```

# Troubleshooting

```
ImportError: /home/martin/miniconda3/envs/VirtualReality/bin/../lib/libstdc++.so.6: version `GLIBCXX_3.4.30' not found (required by /usr/local/lib/libopencv_gapi.so.407)
```

```
conda install -c conda-forge gcc=12.1.0
```

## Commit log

2025-02-04 fix power off
2025-02-20 remove print
2025-02-20 get camera index when recording video
2025-02-25 show param only in camera FOV
2025-03-05 pin opencv version
2025-03-06 use enum for camera model
2025-03-27 remove print statement
2025-04-01 print metadata to file
2025-04-09 dont modify qlabel from another thread
2025-04-11 add temperature sensor
2025-04-14 disable group when no serial device
2025-04-14 add temperature monitor
2025-04-14 add csv name for temperature
2025-04-14 dont print if there is no sensor
2025-04-15 fixing serial sensors
2025-04-24 use kalman filter
2025-05-06 added instructions camera
2025-05-09 fix bugs and implement 3d
    [shell_simplified.obj]
2025-05-27 added kalman filter flag
2025-06-11 print size
2025-06-11 debug print
2025-06-12 comment out debug print
2025-06-12 adding function to generate pink noise filters
2025-06-14 default device
2025-07-02 store board info
2025-07-02 board info
2025-07-02 update board info
2025-07-09 added 24V
2025-07-11 filter relevant stims
2025-07-15 dont print
2025-07-16 wire background polarity
2025-08-20 close thread on exit
2025-08-20 fix thread
2025-08-21 dont overwrite thread
2025-08-31 update GUI with device info
2025-09-01 added instruction fro thorlabs devices
2025-09-05 dont start temperature monitor if no probe connected
2025-09-05 remove stray print
2025-09-08 fix powermeter controls
2025-09-10 added power calibration
2025-09-10 route power cal signal
2025-09-10 added plot power
2025-09-10 integrate power calibration
2025-09-12 set daq board
2025-09-12 allow empty boards
2025-09-12 dont print none
2025-09-25 zoom pan camera preview
2025-10-03 add case
2025-10-31 trying to implement better camera control
2025-11-02 use worker thread to start, stop, record
2025-11-03 implementing new camera widget
2025-11-03 add thread to projector on/off
2025-11-03 disble controls on power on/off
2025-11-03 connect power on cdone
2025-11-03 change new thread name
2025-11-03 run acmera updates in a separate thread
2025-11-04 put everythign in separate thread
2025-11-05 use new widget for cameras
2025-11-06 move to new camera widget
2025-11-13 close camera on preview False
2026-01-27 picospox adpapter files
    [PicoSpoxAdapter_v2-B_Cu.gbr, PicoSpoxAdapter_v2-B_Mask.gbr, PicoSpoxAdapter_v2-B_Paste.gbr, PicoSpoxAdapter_v2-B_Silkscreen.gbr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]
2026-01-27 exclude bom from gitignore
    [bom.csv]
2026-02-06 update bom
    [bom.csv]
2026-02-18 moving cad stuff around
    [MB3045_M-Step.step, PH50_M-Step.step, PH75_M-Step.step, TR50_M-Step.step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]
2026-02-24 adding IR mirror and S120VC
    [bom.csv]
2026-03-11 date cad platform
    [slim_3d_print-Lid_2in.stl, slim_3d_print-Platform_large.stl, slim_3d_print-Platform_small.stl, slim_3d_print.FCStd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]
2026-03-11 added mirror holder
    [mirror_holder_v2-BodyFillet.stl, mirror_holder_v2.FCStd]
2026-03-11 adding files
    [mold_organizer-BodyFillet001.stl, mold_organizer.FCStd]
2026-03-11 1/4'' M6
    [AP25E6M-Step.step]
2026-04-16 ximea camera
2026-04-16 remove file that shouldnt exist and move content around
    [PicoSpoxAdapter_v2-B_Cu.gbr, PicoSpoxAdapter_v2-B_Mask.gbr, PicoSpoxAdapter_v2-B_Paste.gbr, PicoSpoxAdapter_v2-B_Silkscreen.gbr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]
2026-04-29 add stl and rename stp
    [calibration_jig_91mm-BodyChamfer.stl, calibration_jig_91mm.FCStd, step_49159_glass_diffuser.step]
2026-05-09 aravis camera
2026-05-09 adding aravis camera support
2026-05-10 refactored camera widget to debounce inputs
2026-05-10 init camera to default max on creation
2026-05-10 update to CameraSensorROI
2026-05-11 bump camera tool
2026-05-12 bump camera tool version
2026-05-12 crossover cable
    [bom.csv]
2026-05-12 bump camera tools version
2026-05-12 bump camera version
2026-05-12 bump version camera
2026-05-16 bump camera tools
2026-05-19 make camera scrollable
2026-05-19 fix 0 sensor size
2026-05-19 fix camera offset
2026-05-19 test if frame is none
2026-05-21 add number led
2026-05-24 add step file
    [step_64452_cold_mirror.step]
2026-05-25 LED step file
    [ILR-ON16-SC211-WIR200.stp]
2026-05-25 added models
    [GelArena4Wells.stp, PetridishLid.stp]
2026-05-25 add heatsink
    [HeatSink.stp]
2026-05-26 add 3d model cam lens
    [laowa_venus_60mm_f2-8_macro.stl]
2026-05-31 wire loop widget signal to state changed
2026-05-31 set camera state through controller
2026-06-20 dont del camera
2026-06-22 pin numpy
